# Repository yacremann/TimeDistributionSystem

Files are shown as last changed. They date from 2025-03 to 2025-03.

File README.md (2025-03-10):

# Time Distribution System for Lab Based Experiments

This project implements a time distribution system for laboratory based experiments using pulsed lasers.
It consists of a transmitter and several receivers. The transmitter generates a unique pulse-id number for
each laser pulse. This pulse-id, together with configuration information is transmitted to the receivers
over twisted-pair cables (use Cat 6A cables only!). A magnetic RAM is used to store the last value and to
recover after a power outage.

The receivers decode the pulse-id send it to FPGAs on individual instruments (framegrabber boards, digitizers, ...)
for time stamping the data. In addition, the receivers generate low-jitter trigger signals. These can be configured
from the transmitter.

The project contains the following components:
- Boards: Schematics and layouts of the printed circuit boards for the receiver and transmitter
- Firmware: Logic on the FPGAs as well as firmware running on an embedded RISC-V processor for the transmitter and receivers
- Tango: Device servers for the transmitter and to configure the trigger channels of the receivers (see tango-controls.org)
- Notes: Presentation with the block diagrams of the system

## Requirements:
- For simulating the individual components of the firmware: Cocotb, Verilator
- For synthesis: Quartus (intel) v. 23.1 standard edition
- For the software on the RISC-V: gcc for RV32IM (see https://github.com/SpinalHDL/VexRiscv)
- Tango control system: https://tango-controls.org

The project contains the following 3rd party components:
Firmware:
- CRC generator (https://github.com/hellgate202/crc_calc.git)
- Softcore: Based on the VexRiscV project (https://github.com/SpinalHDL/VexRiscv)
- TinyDuino_lib: developed by Domenic Wüthrich as a semester project at ETH Zurich, institute for integrated systems.
- fifo_v3: https://github.com/pulp-platform/common_cells/blob/master/src/fifo_v3.sv (ETH Zurich and University of Bologna)

License:
GNU Public License v3.0 (see LICENSE)

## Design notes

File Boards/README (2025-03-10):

This is the schematic and layout of the time distribution system. It consists of a transmitter and a receiver board. A detailed description will be published in a paper.

This part has been developed by Jingo Bozzini and Yves Acremann at the Physics Department of ETH Zurich, Switzerland.
acremann@solid.phys.ethz.ch

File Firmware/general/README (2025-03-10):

These components are often used by both, the receiver and transmitter (or by the receiver included in the framegrabber or digitizer).

8b10b: 8b 10b encoder / decoder
async_fifo: Async FIFO from https://github.com/dpretet/async_fifo (Copyright 2017 Damien Pretet ThotIP; See Github repo)
APB: Implementation of the APB bus and bus registers in SystemVerilog using interfaces.
CRC: CRC generator from https://github.com/hellgate202/crc_calc (Leonid Ivanov)
FrameReceiver: The receiver for decoding a data frame
FrequencyCounter: Used to measure the frequency of the laser oscillator
PayloadTransmitter: Prepares a data frame for serialization. It also calculates the CRC and performs 8b10b encoding.
protocol: The include file defining the data structure of a data frame
pulse_extender: Used to make the LEDs blink long enough in case of an error
SlowLink: Implements the slow transmitter (for sending data to the framegrabber) as well as CDR for the receiver in the framegrabber
Softcore: Microcontroller based on the VexRISCV CPU running on teh transmitter and receiver
Trigger: Circuit to generate the trigger sgnals at the output of the receiver
watchdog: Simple watchdog circuit to reset the receiver in case of a sequence of errors
FIFO: Fifo to cross clock domain boundaries (Copyright 2018 ETH Zurich and University of Bologna, https://github.com/pulp-platform/common_cells)

Most modules include a test bench using Cocotb and Verilator. These can be run using the Makefiles.

tinyduino_lib: Drivers for the components of the softcore (from Dominic Wüthrich, 2021)

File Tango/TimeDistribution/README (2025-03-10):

This is the Tango device server to control the time distribution
system through the USB port of the transmitter. It allows for 
configuring the receiver and setting the parameters of the
trigger outputs of the receivers.

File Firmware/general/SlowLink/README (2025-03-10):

This code implements the slow link between the receiver box and the receiver on the custom configurable FPGA on the frame grabber / digitizer.

It also contains test benches for simulating the CRD loop (50 MHz, 250 MHz and 312 MHz clock frequency) using Cocotb and Verilator.

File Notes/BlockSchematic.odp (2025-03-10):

## Block schematic

Low jitter time distribution system,

Y. Acremann, 2.2.2021

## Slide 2

Config data

80 MHz clk

Pulse-ID

100 Hz

M-RAM

MR25H128

FPGA

(MAX 10)

Logic,

CPU

LVDS to LVCMOS

SN65LVDS4

Transmitter

SPI

For precision receivers

80 MHz

AD9543

(jitter cleaner,

clk distribution)

SPI

Pulse-ID

8b/10b

Serializer

SCAN-

921025H

Fan-out

buffer

NB3L8504S

driver

DS15BA101

RJ-45

cable

driver

DS15BA101

RJ-45

cable

100 Hz

driver

DS15BA101

RJ-45

cable

UART,

JTAG

(CPU)

USB – Serial

FT2232

(for debugging)

driver

DS15BA101

RJ-45

cable

USB

800 Mbit/s signals with embedded clock

## Concept

- Bit clock synchronized to the oscillator (80 MHz) for precision timing (estimate: 10 ps jitter)
- Jitter cleaner to get very clean clock signals from 80 MHz clock
- FPGA:
- Counting of 100 Hz pulses (pulse-ID)
- Control of the serializer and M-RAM
- CPU for configuration of the jitter cleaner
- M-RAM: Stores the last pulse-ID (restore after power-loss)
- Distribution: RJ-45 cabes, max. length: 70m
- Encoding:
- For simple receivers: 10 Mbit/s 8b/10b encoded data => jitter: 100 ns
- For precision receivers: 800 Mbit/s 8b/10b encoded data (+ start bit)

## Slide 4

Config data (not time critical)

80 MHz clk

Pulse-id

100 Hz

Receiver

USB – Serial

FT2232

(for debugging)

FPGA

(MAX 10)

Logic,

CPU

USB

Input

RJ-45

cable

receiver (2x)

DS15EA101

De-Serializer

SCAN-

921226H

Pulse-id

Trigger

Time stamp

(to frame grabber)

Lock

AD9543

(jitter cleaner,

clk distribution)

SPI

RJ-45

cable

driver (2x)

DS15BA101

Low-jitter

trigger

Output to another receiver

LVDS to LVCMOS

SN65LVDS4

## Additional features: Receiver

- Power over the RJ-45 cable to the receivers
- Trigger outputs:
- Several independent outputs
- Low jitter
- Time steps in 1/(80 MHz)
- Output connector to connect another receiver

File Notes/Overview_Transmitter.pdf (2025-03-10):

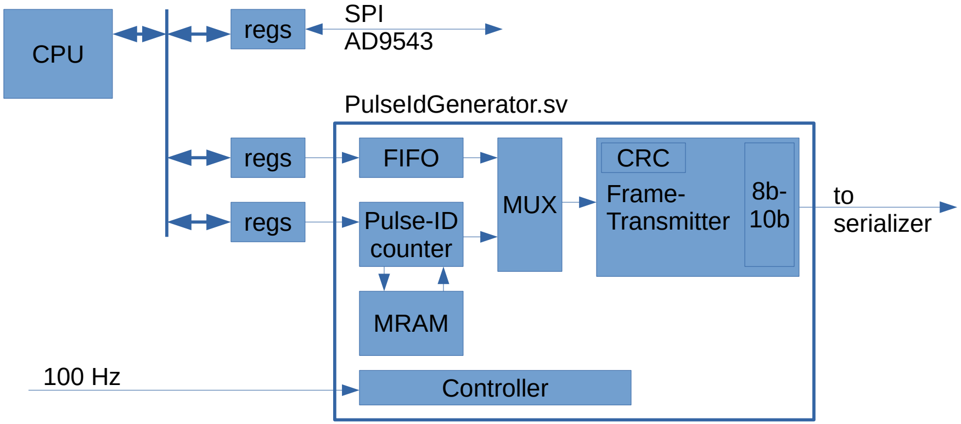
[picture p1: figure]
FIFO; Pulse-ID counter; MRAM; MUX; Controller; Frame- Transmitter; CRC; CPU; regs; to serializer; PulseIdGenerator.sv; SPI AD9543

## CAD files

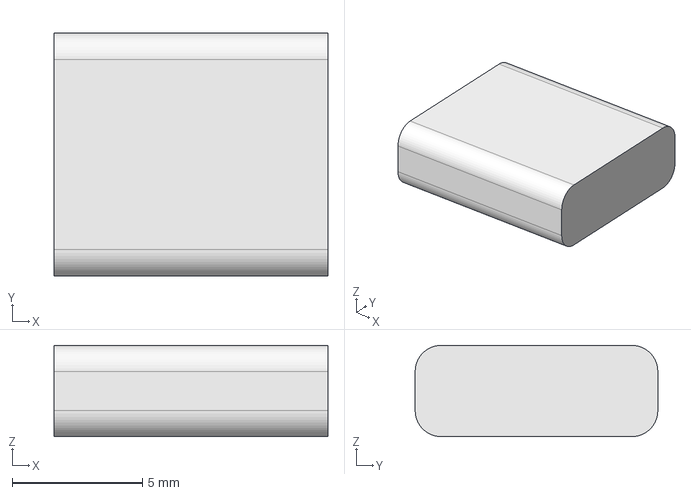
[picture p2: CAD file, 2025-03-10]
Boards/Receiver/3D_files/USB_C.step
10.5 x 9.30 x 3.50 mm

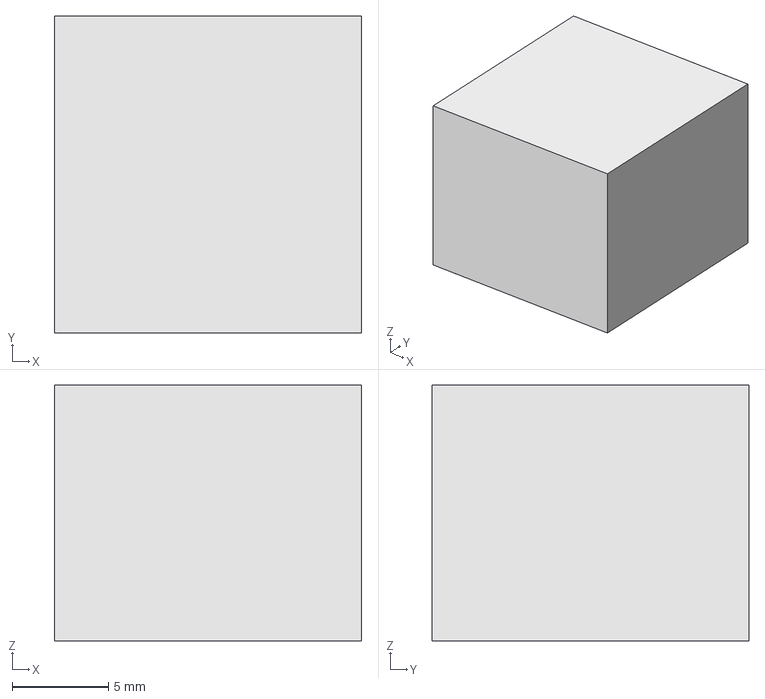
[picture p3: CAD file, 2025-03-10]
Boards/Transmitter/3D_files/RJ45.step
16.0 x 16.5 x 13.3 mm

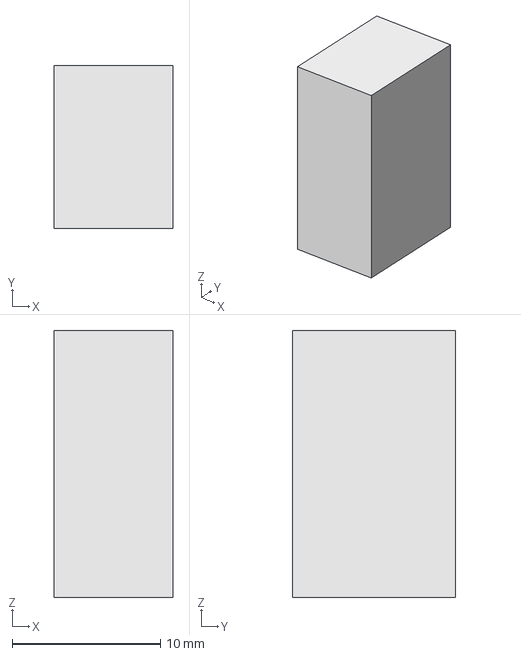
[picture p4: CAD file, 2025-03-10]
Boards/Transmitter/3D_files/conn_3.81mm.step
8.00 x 11.0 x 18.0 mm

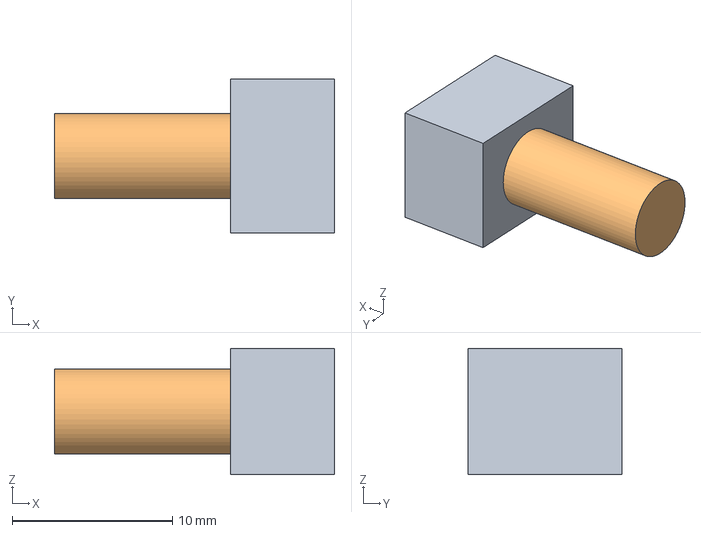
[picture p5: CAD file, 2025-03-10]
Boards/Receiver/3D_files/conn_sma.step
17.5 x 9.60 x 7.90 mm

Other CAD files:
Firmware/IdReceiver_DE10Lite/stp4.stp
Boards/Receiver/3D_files/RJ45.FCStd
Boards/Receiver/3D_files/USB_C.FCStd
Boards/Receiver/3D_files/conn_3.81mm.FCStd
Boards/Receiver/3D_files/conn_sma.FCStd
Boards/Transmitter/3D_files/RJ45.FCStd
Boards/Transmitter/3D_files/conn_3.81mm.FCStd

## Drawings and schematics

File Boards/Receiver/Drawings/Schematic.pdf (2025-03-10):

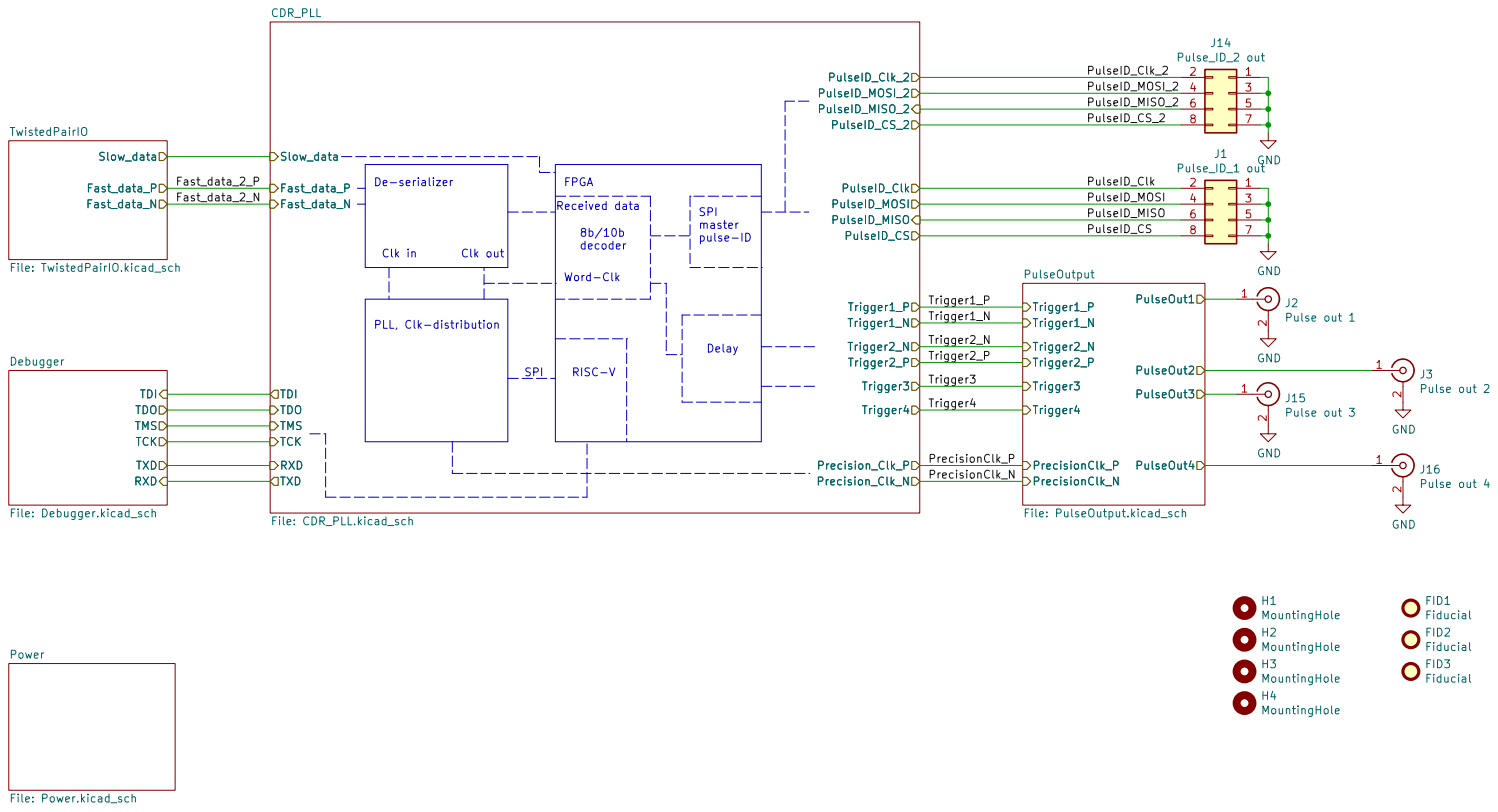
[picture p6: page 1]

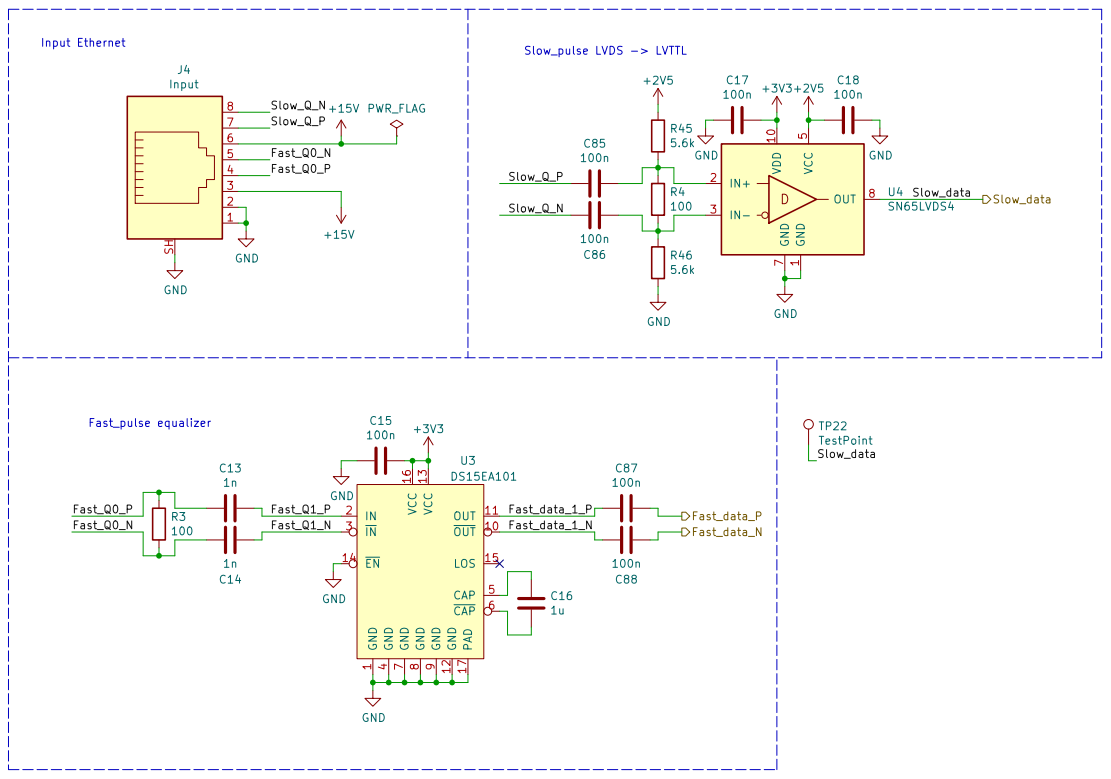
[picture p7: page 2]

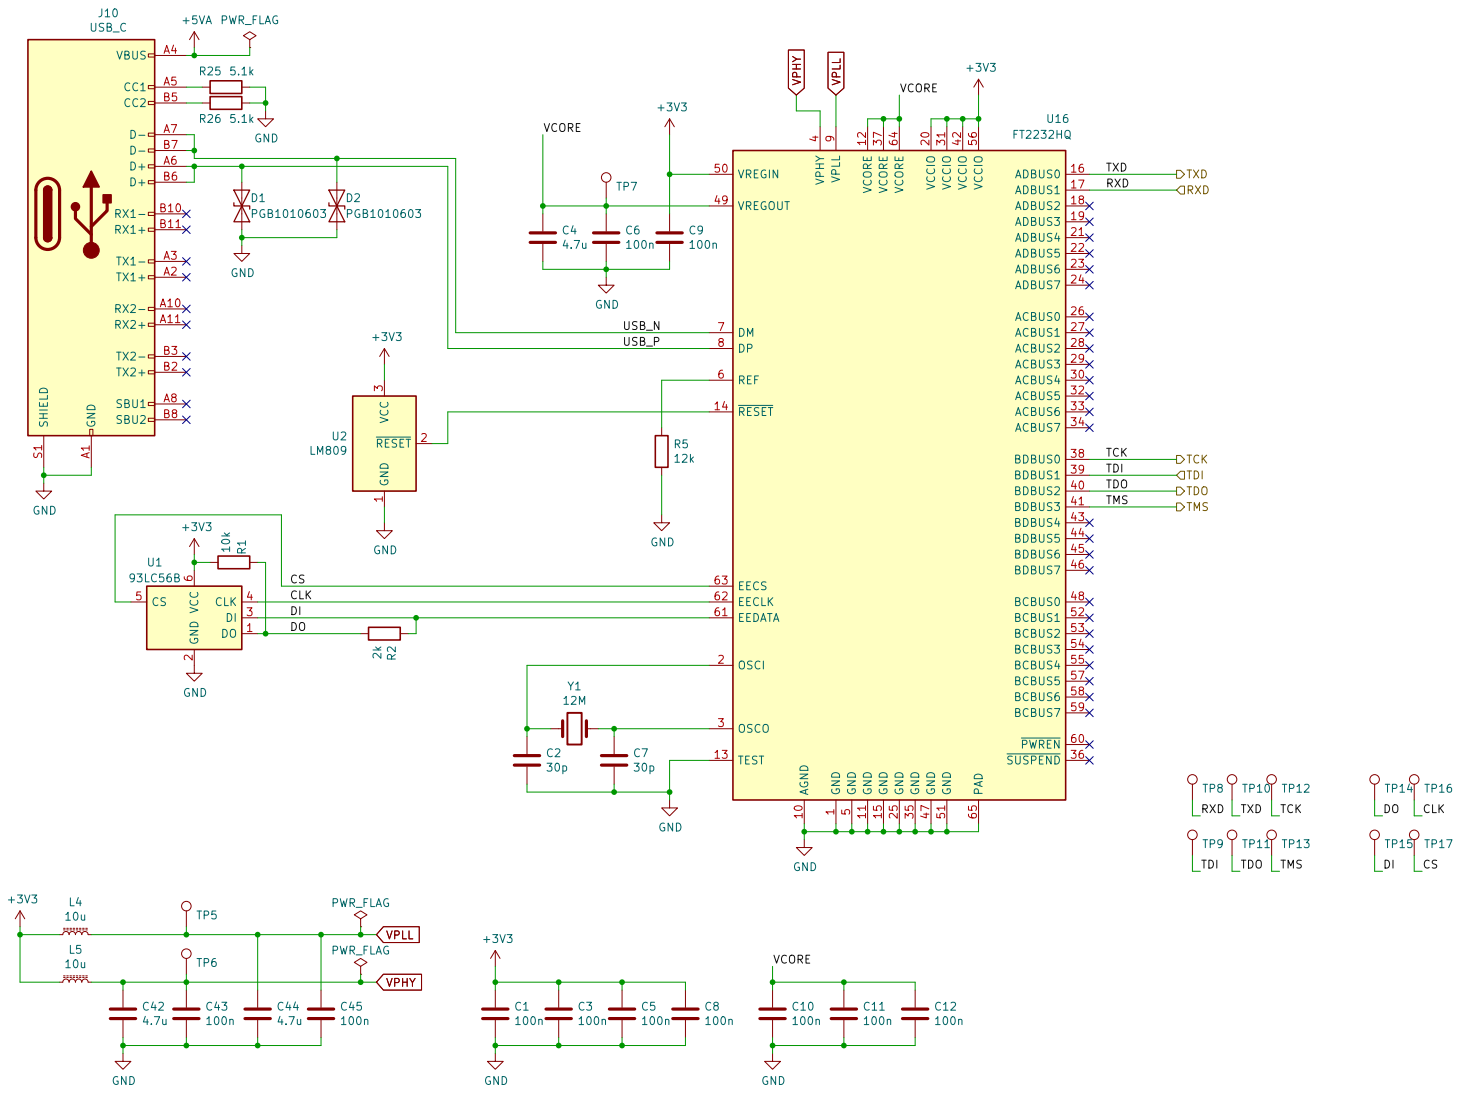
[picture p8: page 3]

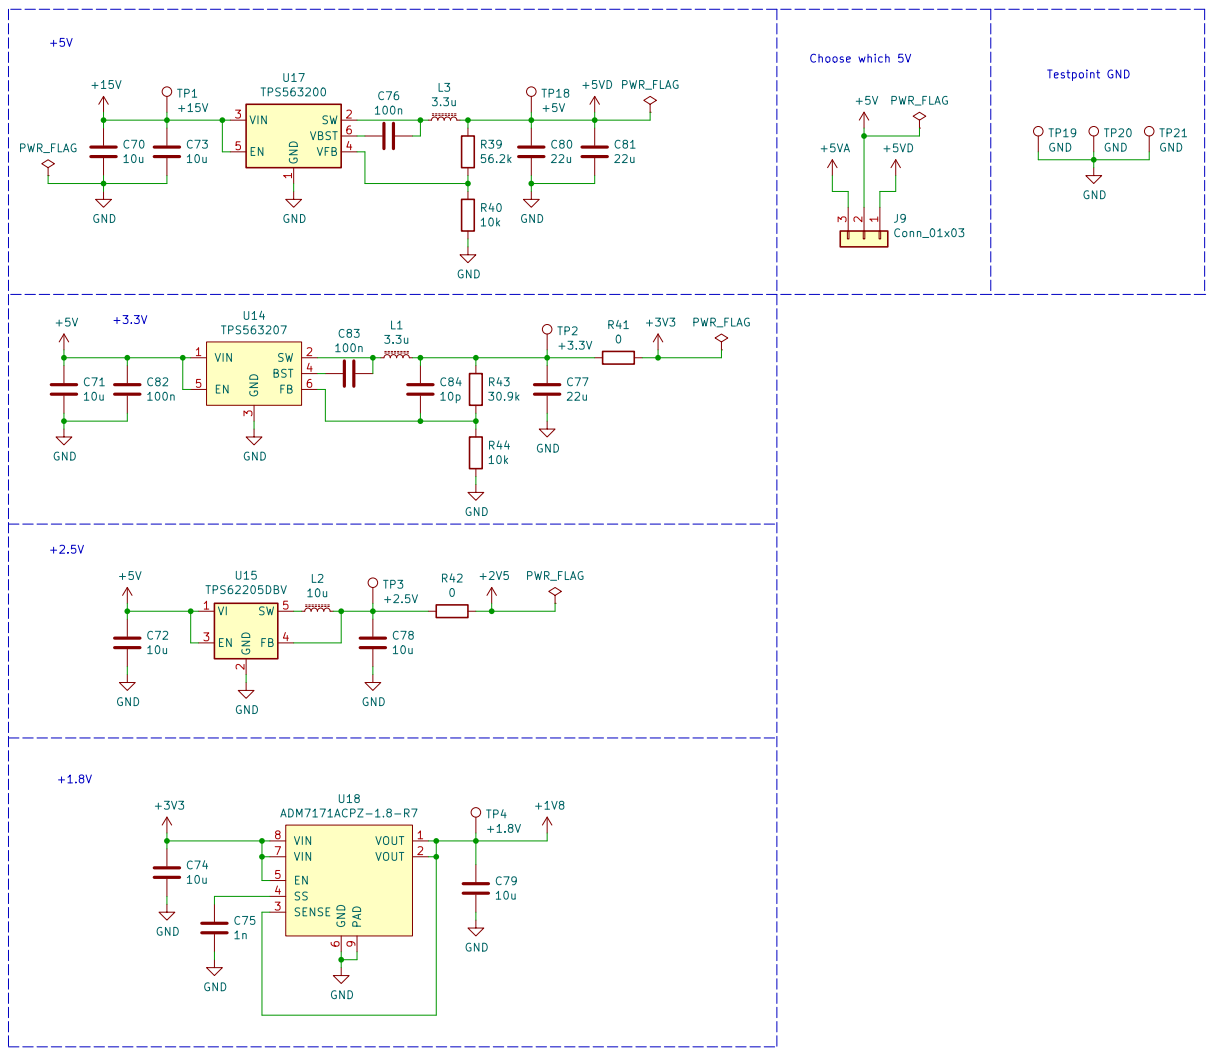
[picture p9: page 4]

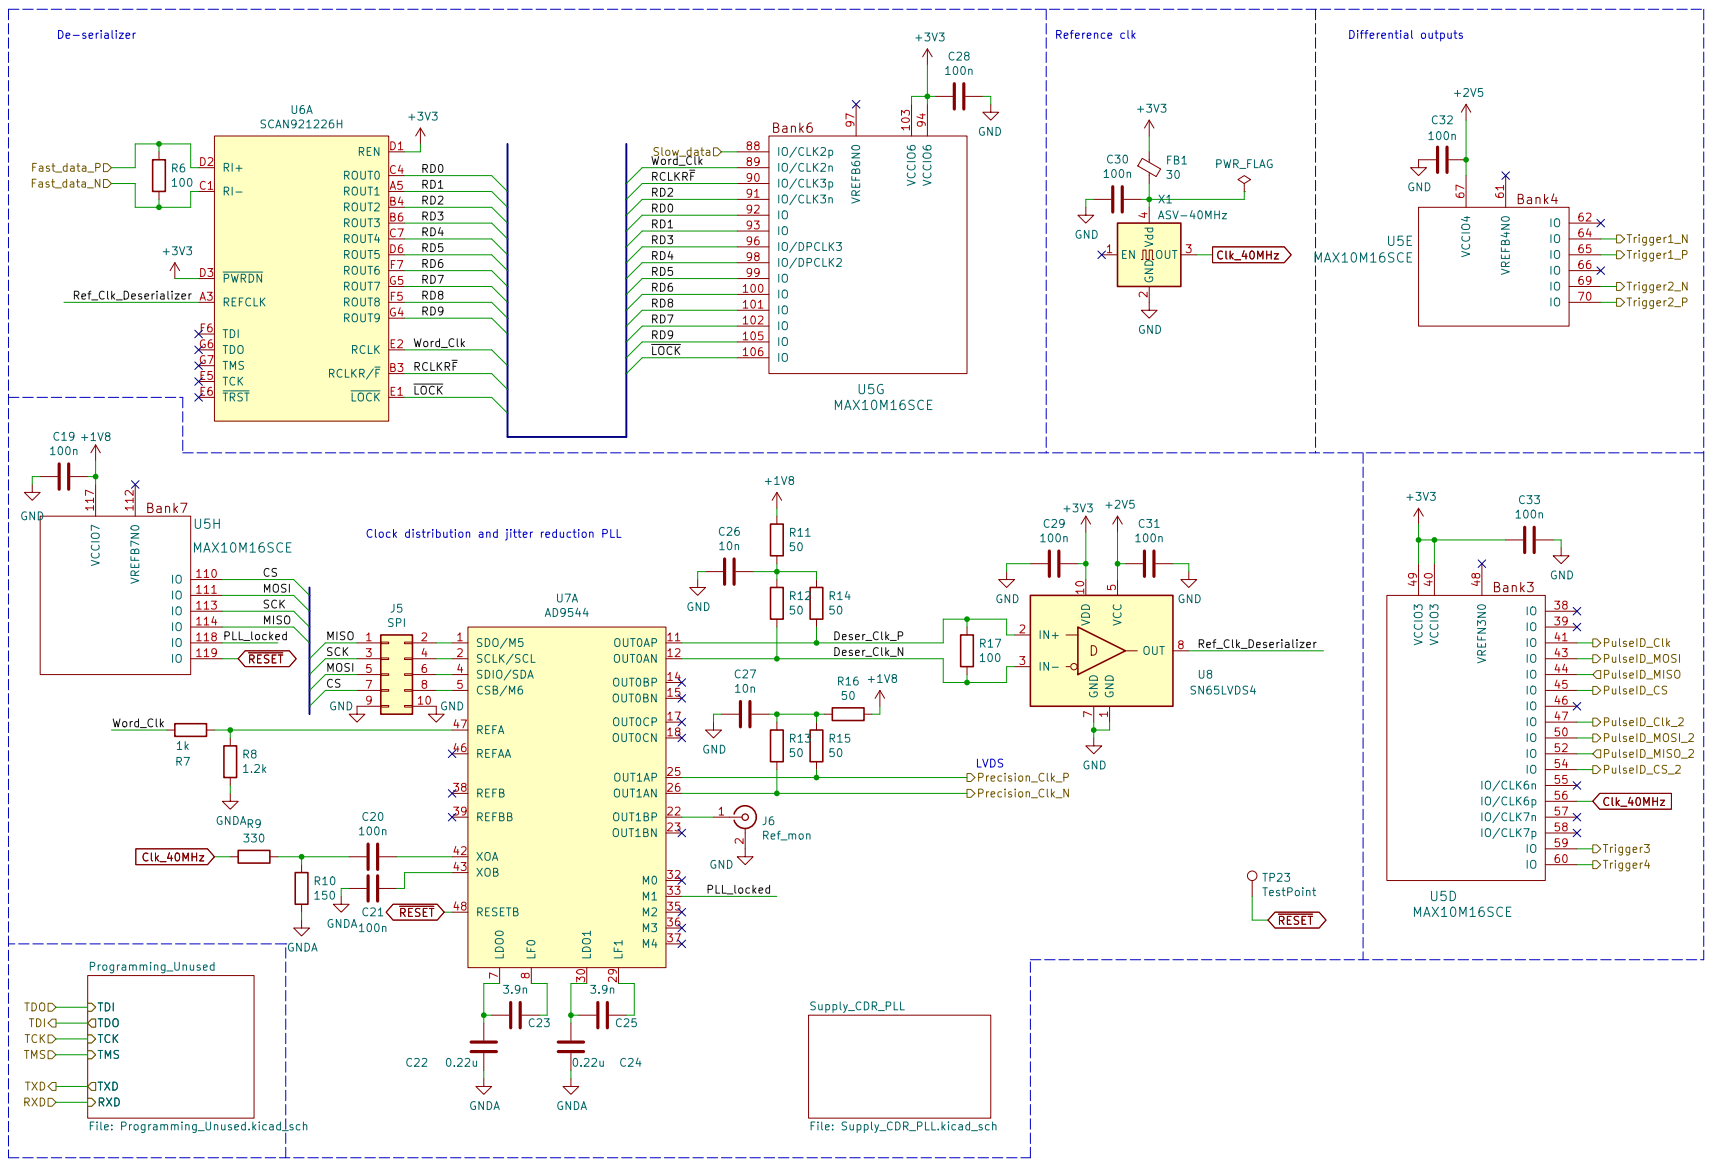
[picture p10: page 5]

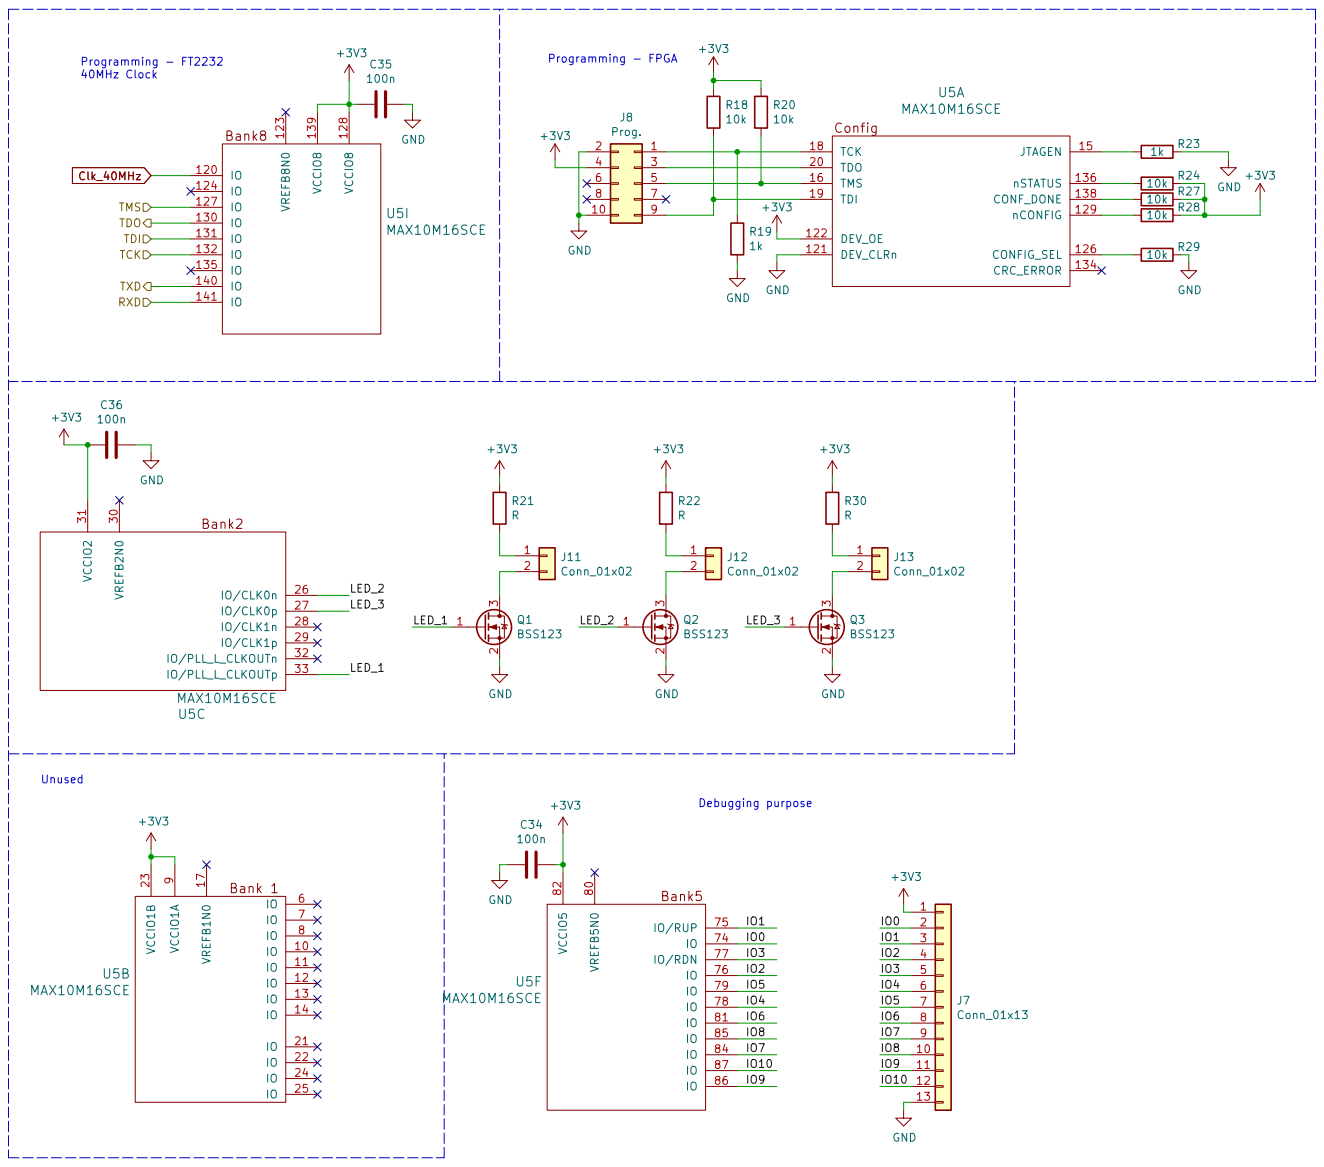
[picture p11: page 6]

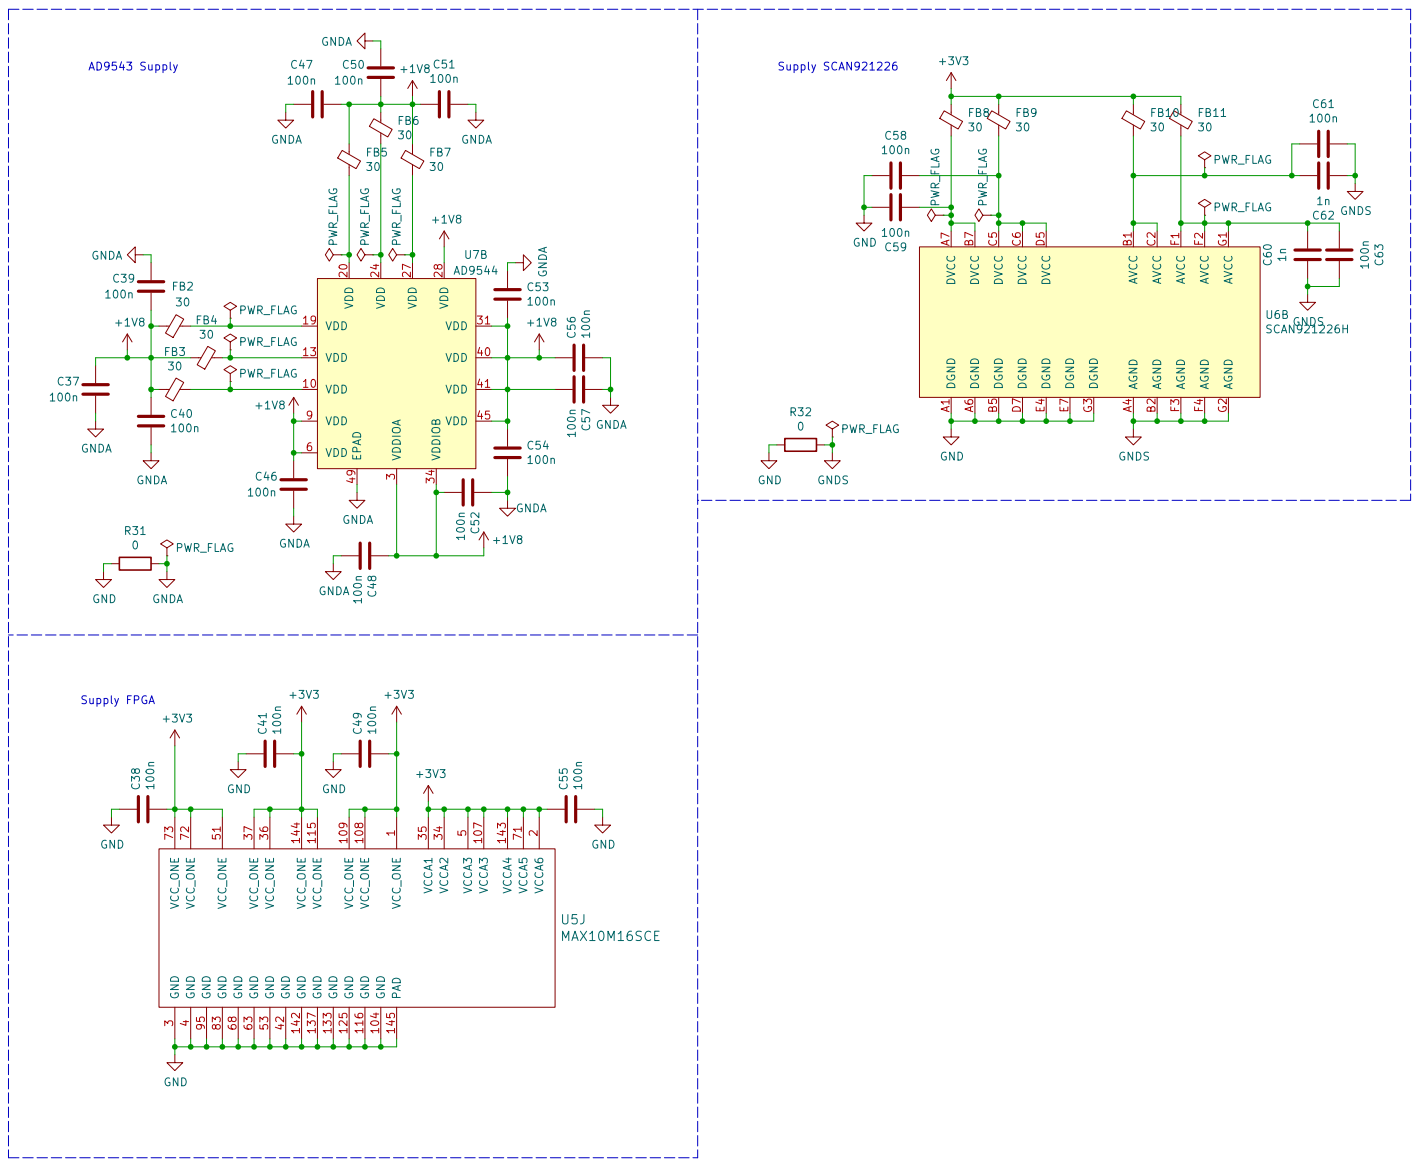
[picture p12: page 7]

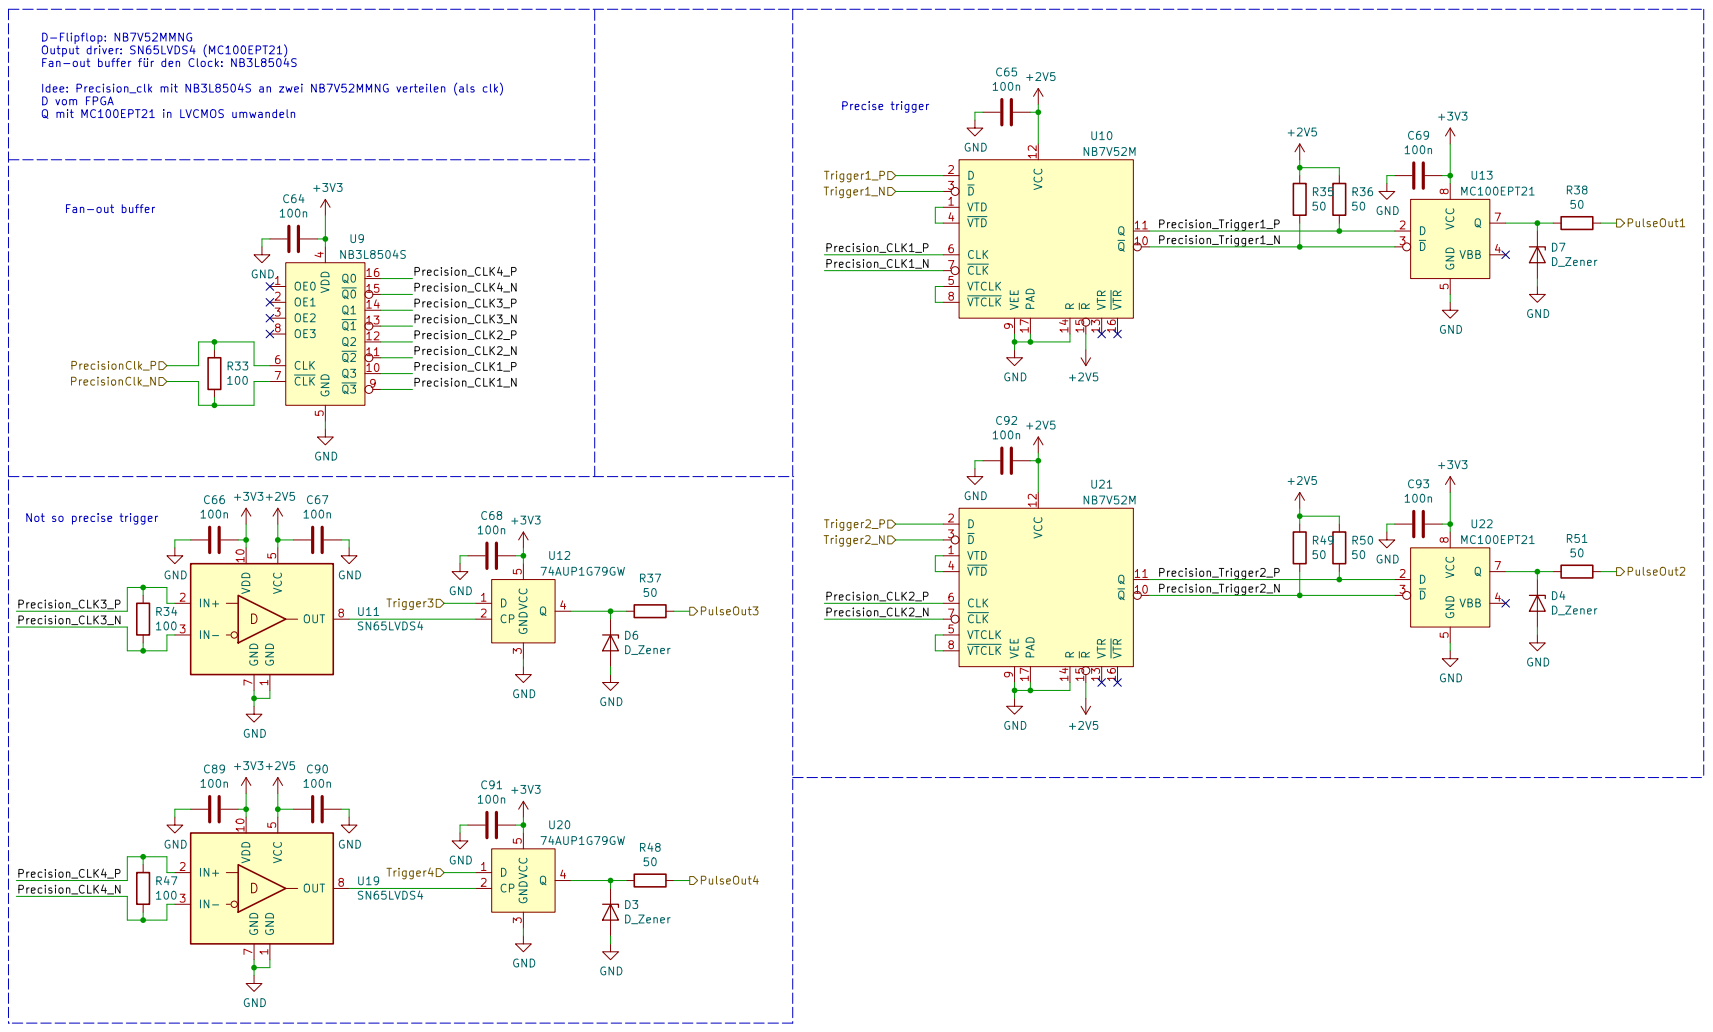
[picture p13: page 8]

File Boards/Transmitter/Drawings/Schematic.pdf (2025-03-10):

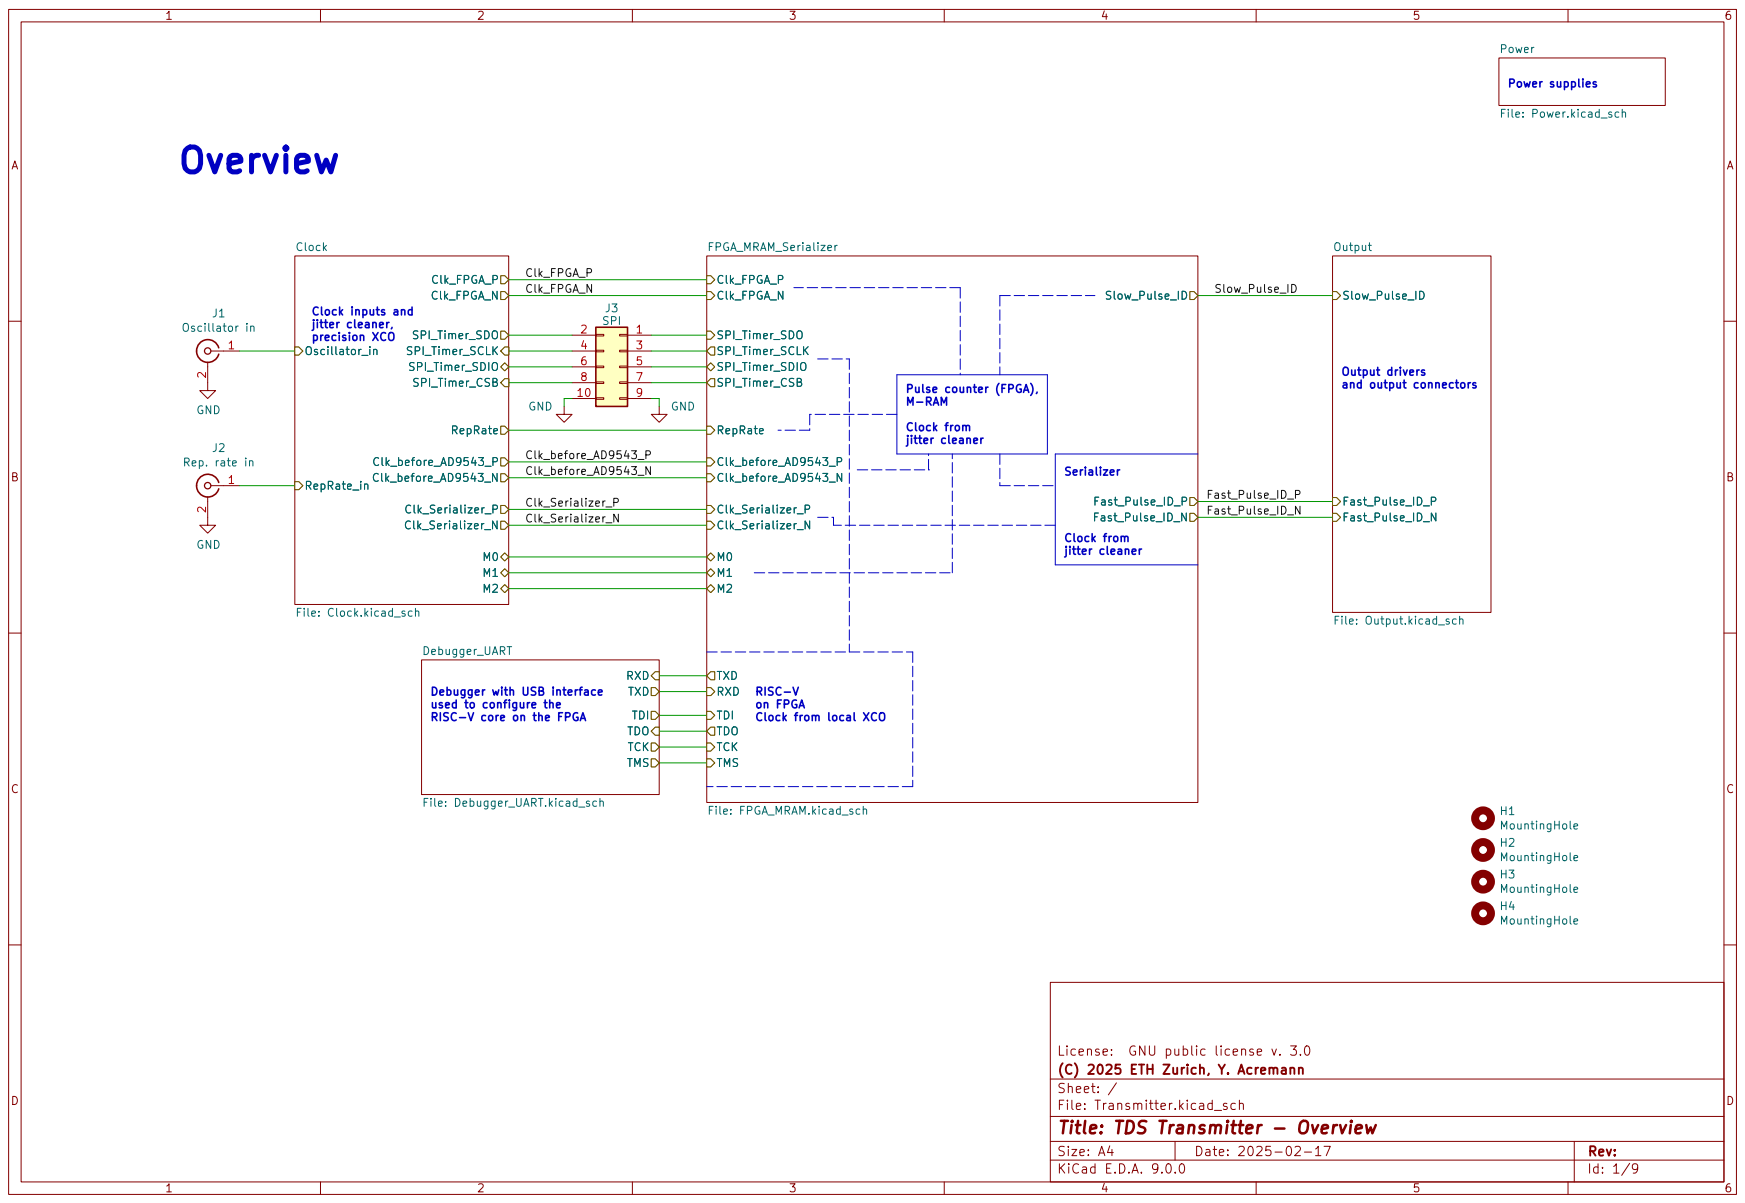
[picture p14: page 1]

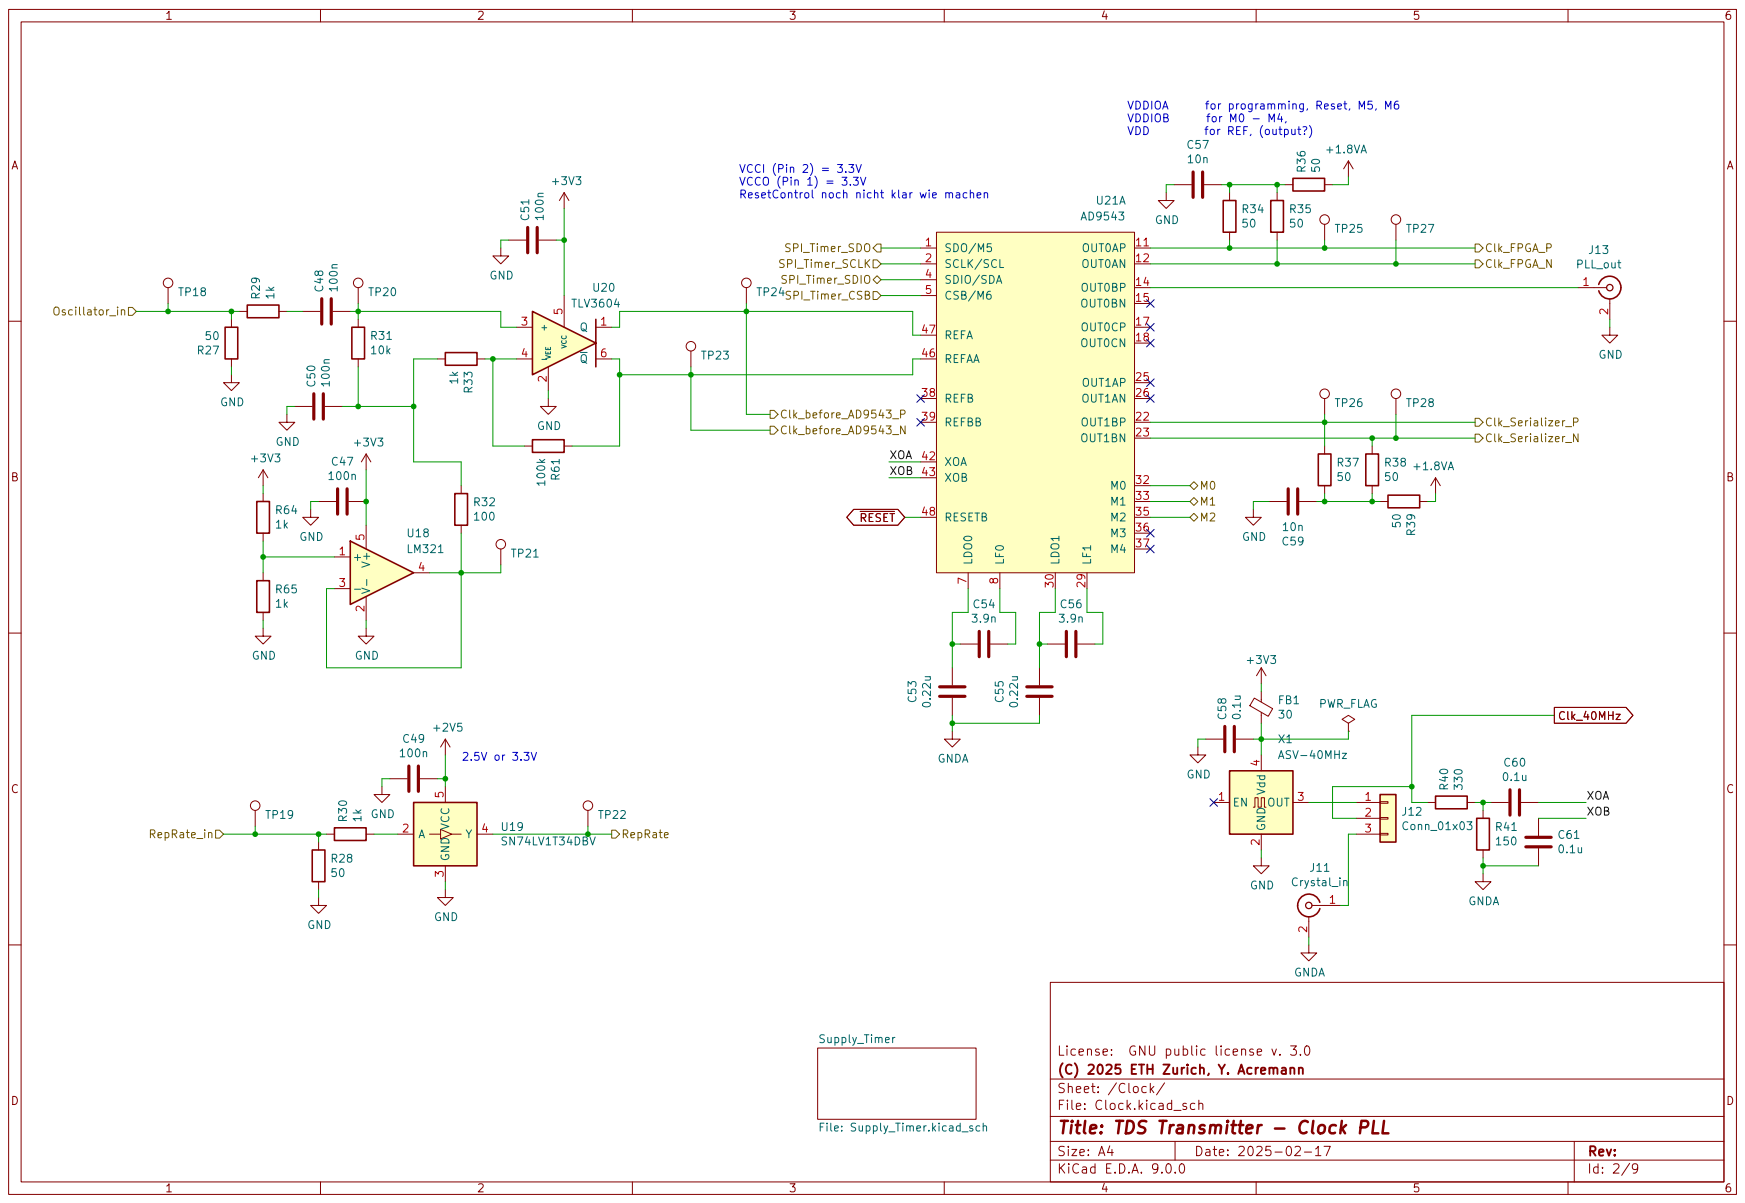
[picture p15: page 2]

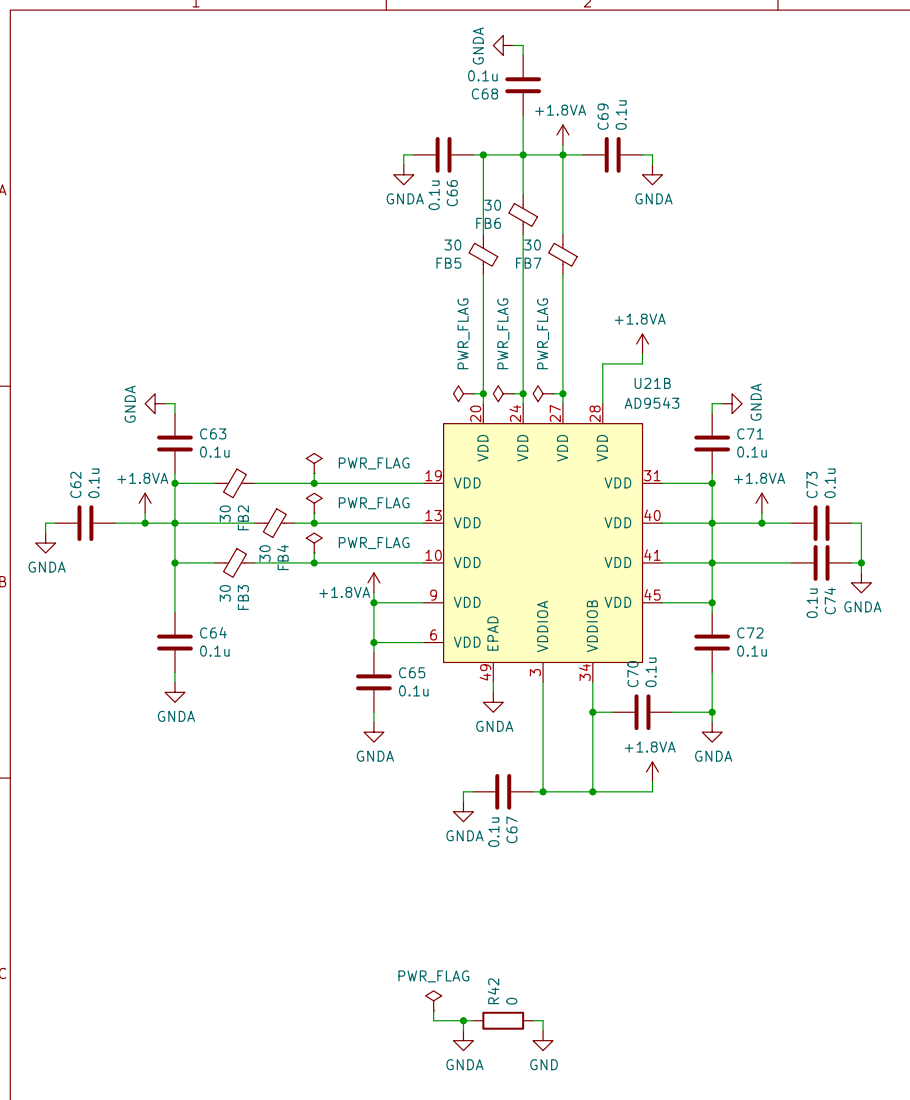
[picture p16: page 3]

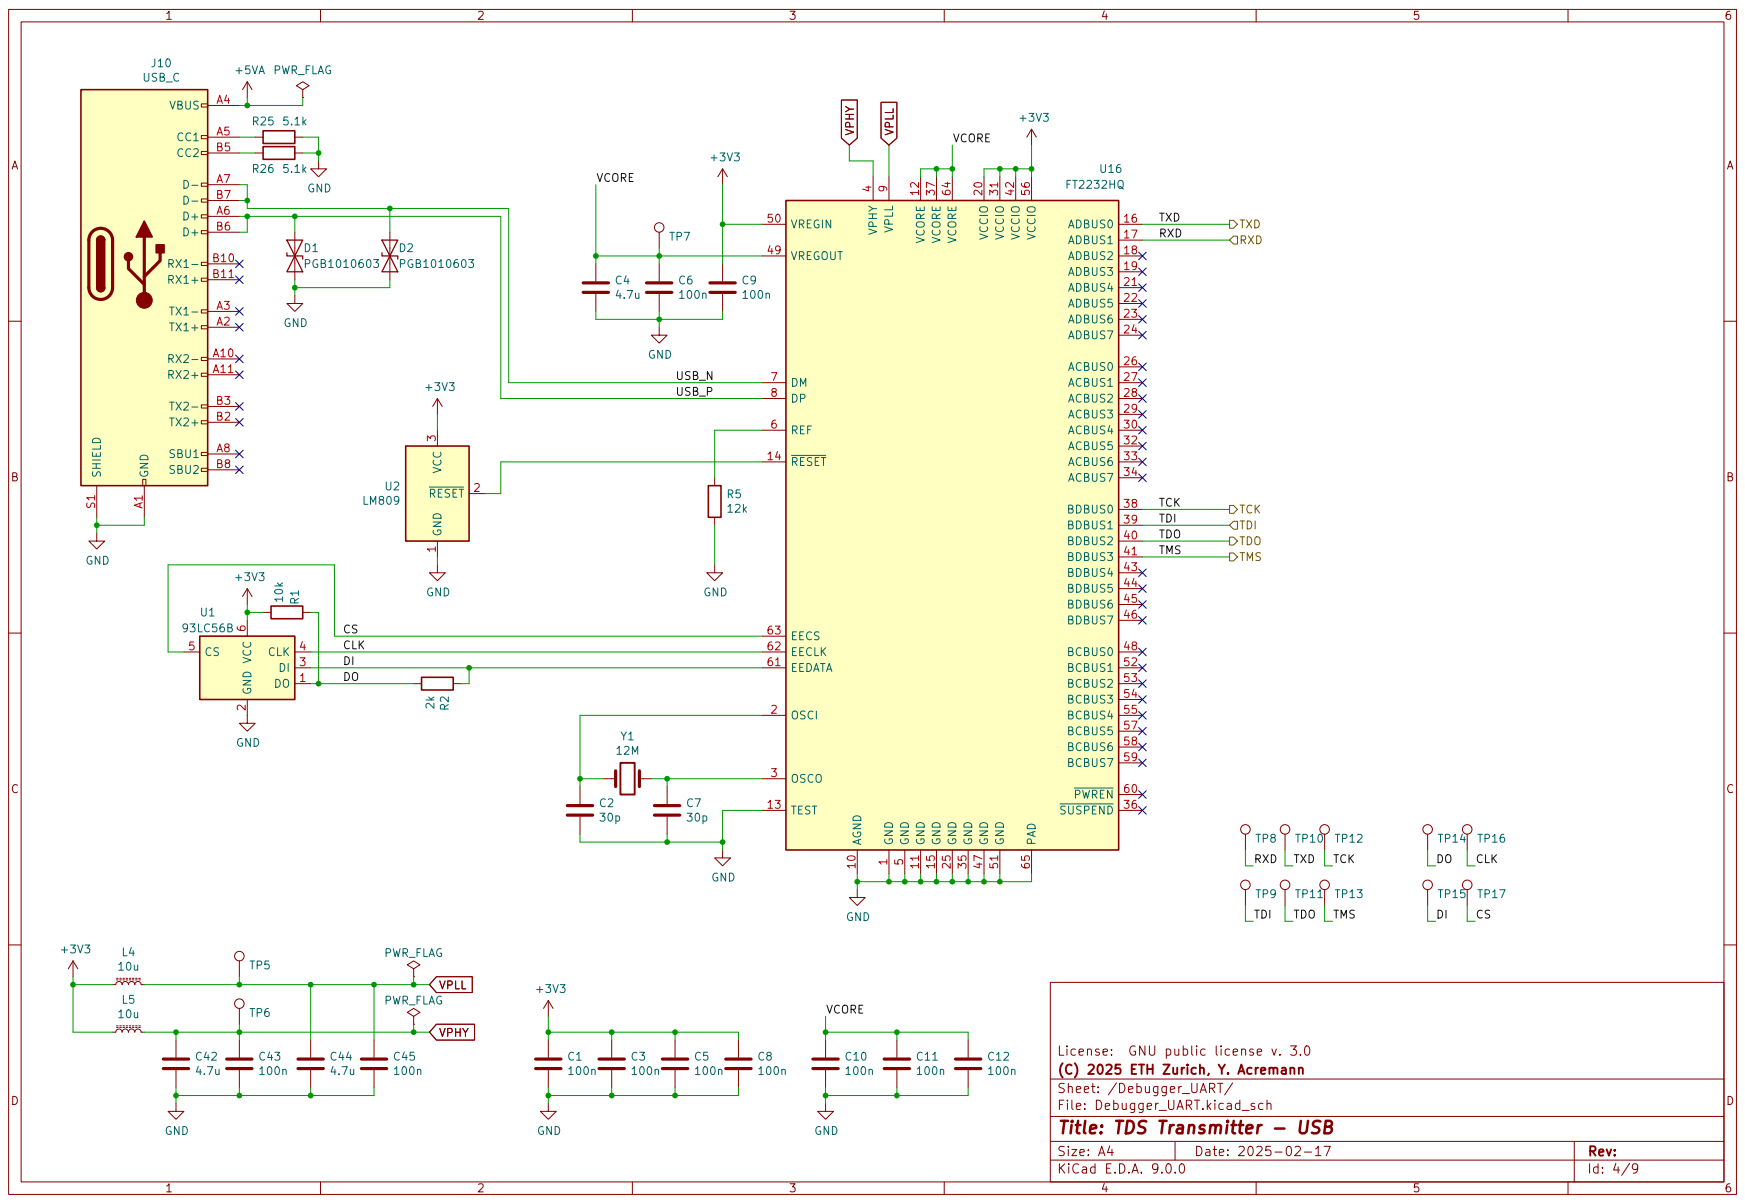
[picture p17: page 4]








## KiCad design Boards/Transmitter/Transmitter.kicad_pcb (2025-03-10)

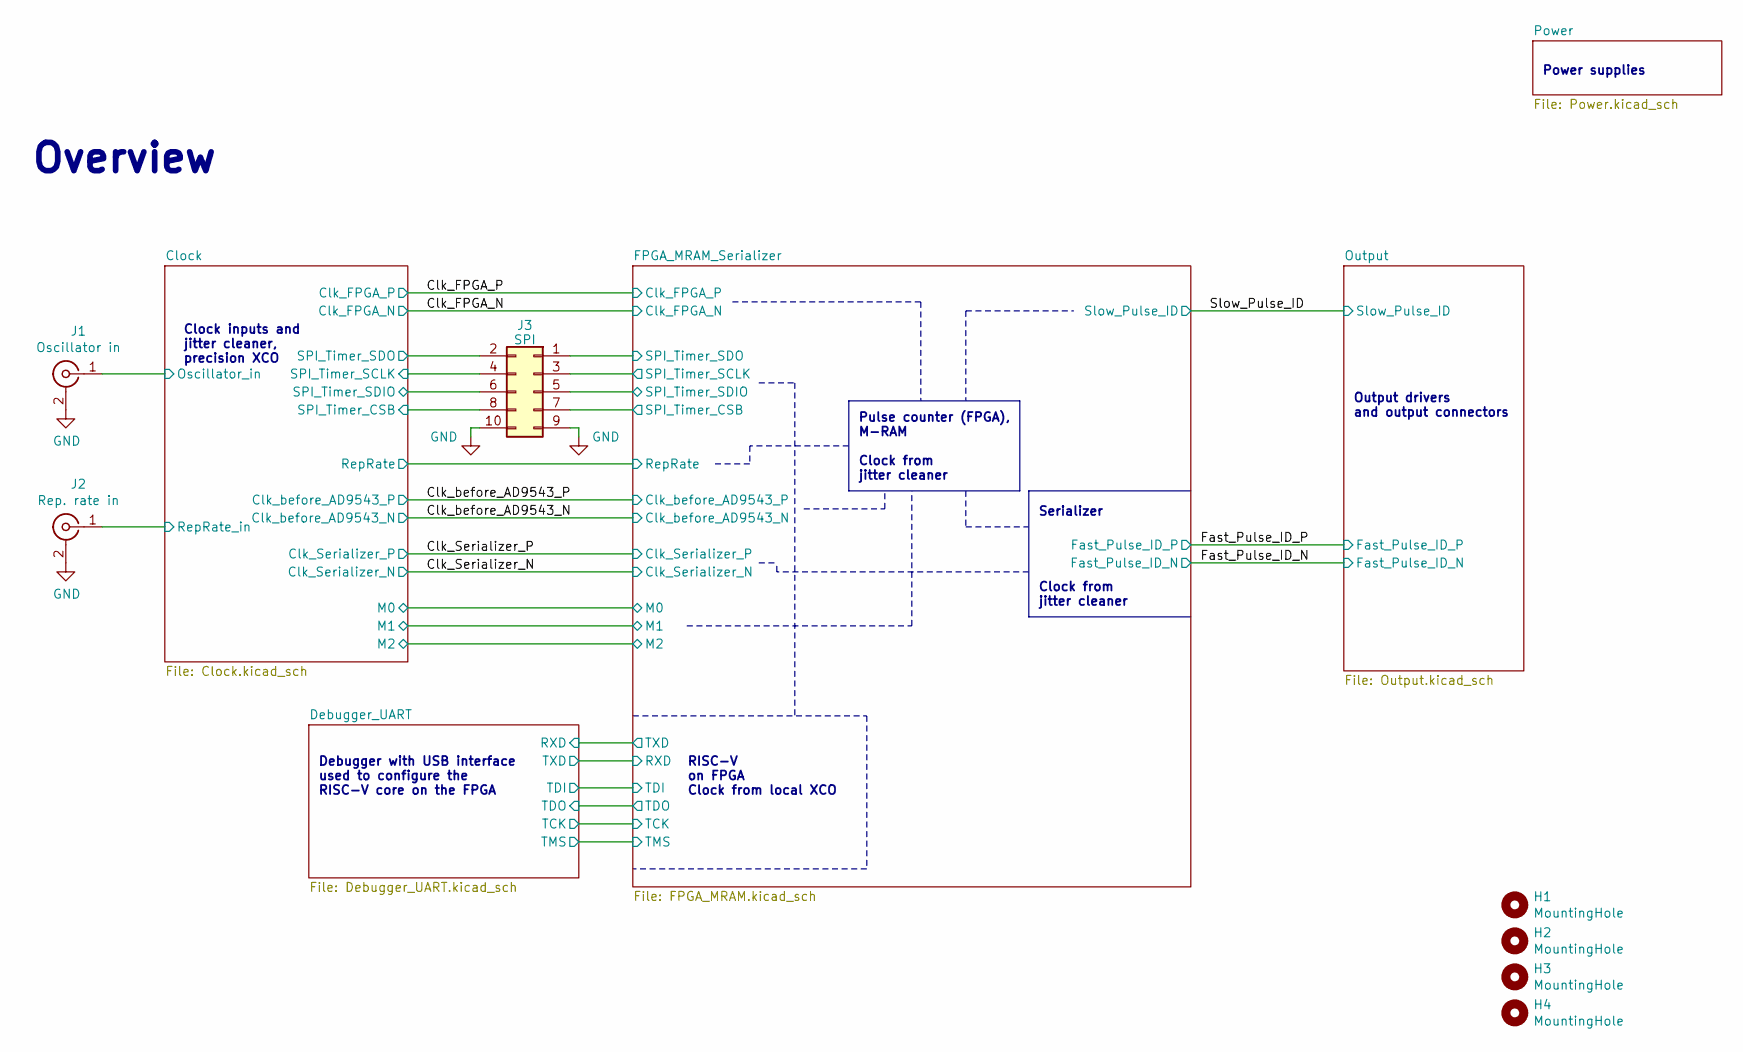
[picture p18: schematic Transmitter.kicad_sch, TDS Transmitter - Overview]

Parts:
H1, H2, H3, H4: MountingHole; MountingHole_2.7mm_M2.5
J1: Oscillator in; SMA_Amphenol_132289_EdgeMount
J2: Rep. rate in; SMA_Amphenol_132289_EdgeMount
J3: SPI; PinHeader_2x05_P2.54mm_Vertical

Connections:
/Clock/Oscillator_in: J1.1 (In); also elsewhere on the board
/Clock/RepRate_in: J2.1 (In); also elsewhere on the board
/Clock/SPI_Timer_CSB: J3.8; also elsewhere on the board
/Clock/SPI_Timer_SCLK: J3.4; also elsewhere on the board
/Clock/SPI_Timer_SDIO: J3.6; also elsewhere on the board
/Clock/SPI_Timer_SDO: J3.2; also elsewhere on the board
/FPGA_MRAM_Serializer/SPI_Timer_CSB: J3.7; also elsewhere on the board
/FPGA_MRAM_Serializer/SPI_Timer_SCLK: J3.3; also elsewhere on the board
/FPGA_MRAM_Serializer/SPI_Timer_SDIO: J3.5; also elsewhere on the board
/FPGA_MRAM_Serializer/SPI_Timer_SDO: J3.1; also elsewhere on the board
GND: J1.2 (Ext), J2.2 (Ext), J3.9, J3.10; also elsewhere on the board

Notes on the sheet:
RISC-V on FPGA Clock from local XCO
Pulse counter (FPGA), M-RAM Clock from jitter cleaner
Clock inputs and jitter cleaner, precision XCO
Clock from jitter cleaner
Overview
Power supplies
Debugger with USB interface used to configure the RISC-V core on the FPGA
Output drivers and output connectors
Serializer

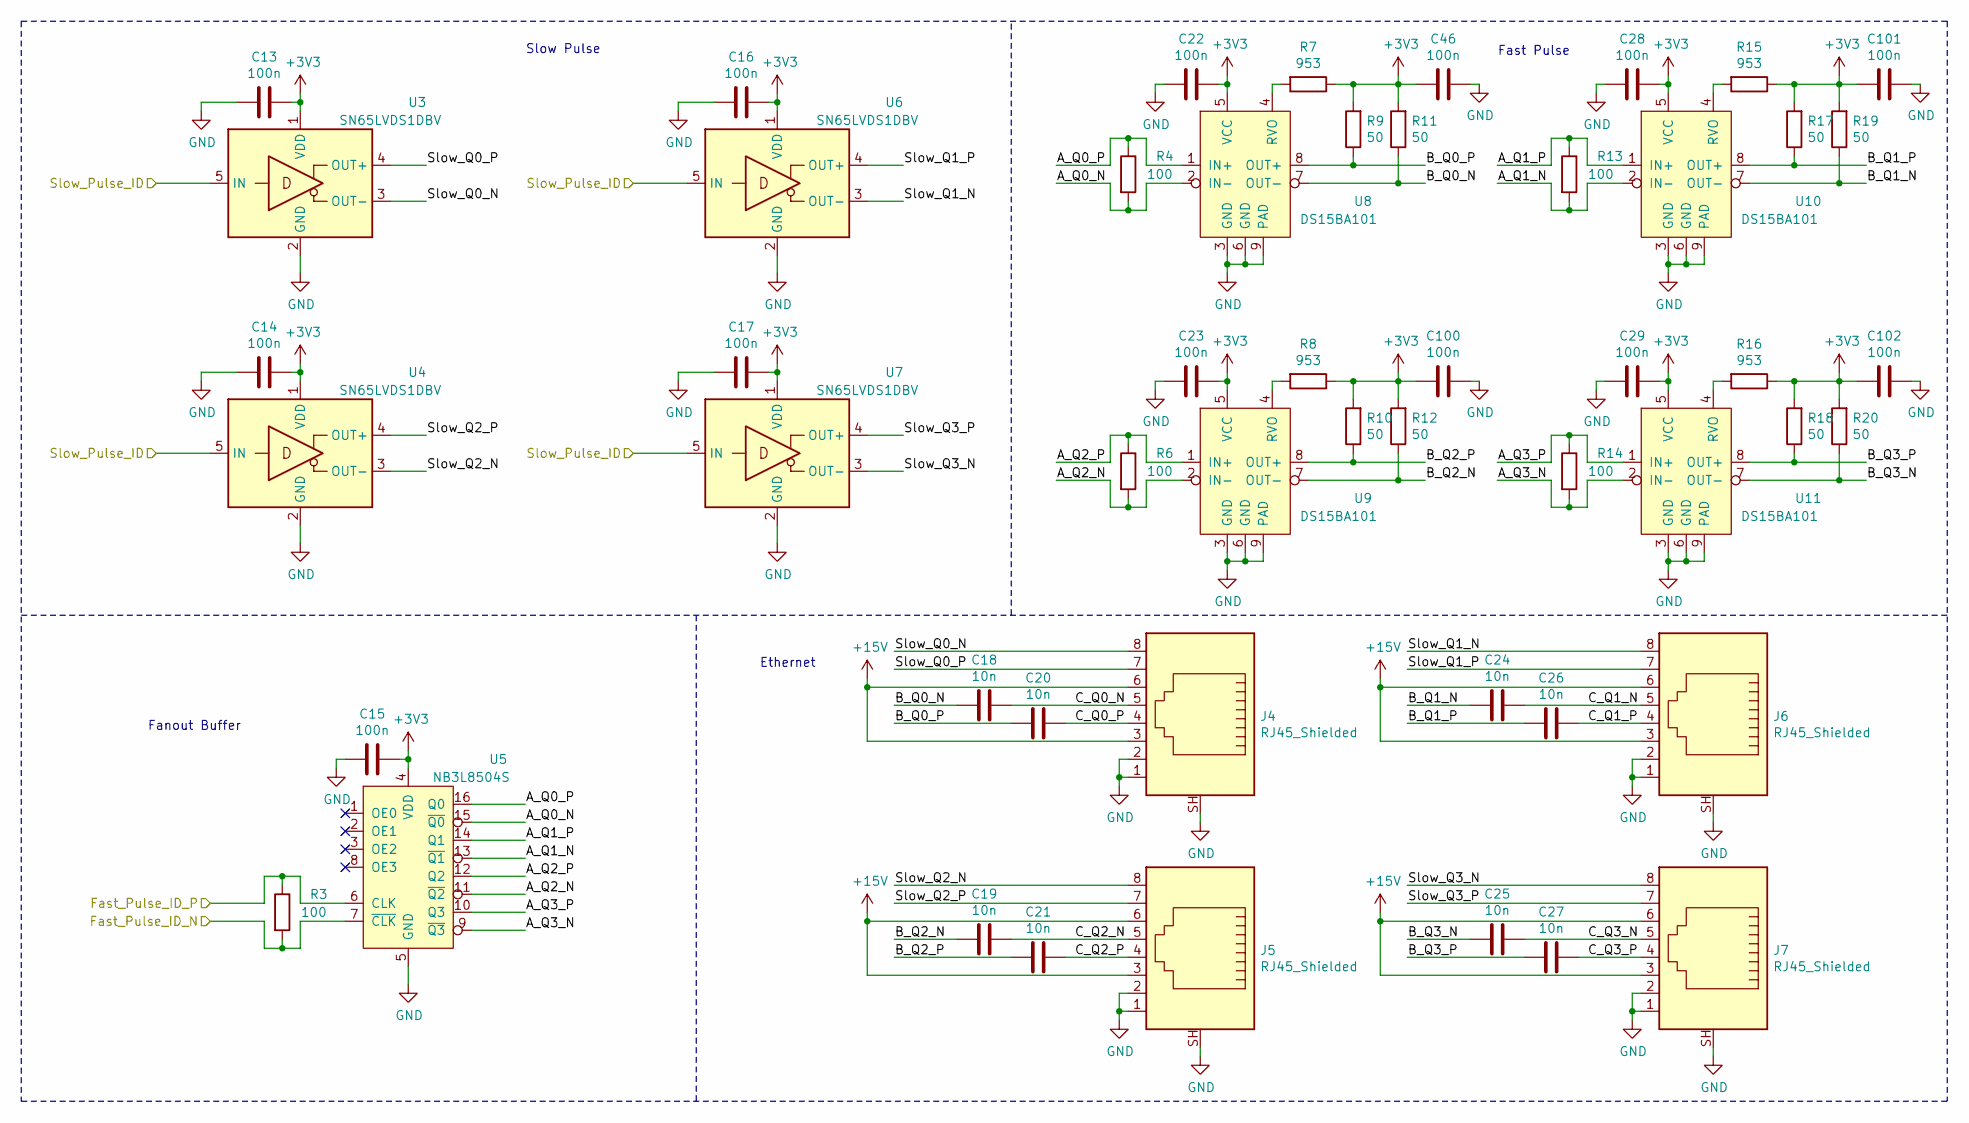
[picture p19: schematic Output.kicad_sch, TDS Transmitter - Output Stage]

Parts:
C13, C14, C15, C16, C17, C22, C23, C28, C29, C46, C100, C101, C102: 100n; C_0603_1608Metric
C18, C19, C20, C21, C24, C25, C26, C27: 10n; C_0603_1608Metric
J4, J5, J6, J7: RJ45_Shielded; RJ45_Amphenol_RJHSE5380
R3, R4, R6, R13, R14: 100; R_0402_1005Metric
R7, R8, R15, R16: 953; R_0603_1608Metric
R9, R10, R11, R12, R17, R18, R19, R20: 50; R_0603_1608Metric
U3, U4, U6, U7: SN65LVDS1DBV; SOT-23-5
U5: NB3L8504S; TSSOP-16_4.4x5mm_P0.65mm
U8, U9, U10, U11: DS15BA101; WSON-8-1EP_3x3mm_P0.5mm_EP1.6x2.0mm

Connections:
+3V3: C13.1, C14.1, C15.1, C16.1, C17.1, C22.1, C23.1, C28.1, C29.1, C46.2, C100.2, C101.2, C102.2, R7.1, R8.1, R9.2, R10.2, R11.2, R12.2, R15.1, R16.1, R17.2, R18.2, R19.2, R20.2, U3.1 (VDD), U4.1 (VDD), U5.4 (VDD), U6.1 (VDD), U7.1 (VDD), U8.5 (VCC), U9.5 (VCC), U10.5 (VCC), U11.5 (VCC); also elsewhere on the board
+15V: J4.3, J4.6, J5.3, J5.6, J6.3, J6.6, J7.3, J7.6; also elsewhere on the board
/Fast_Pulse_ID_N: R3.2, U5.7 (~CLK); also elsewhere on the board
/Fast_Pulse_ID_P: R3.1, U5.6 (CLK); also elsewhere on the board
/Output/A_Q0_N: R4.2, U5.15 (~Q0), U8.2 (IN-)
/Output/A_Q0_P: R4.1, U5.16 (Q0), U8.1 (IN+)
/Output/A_Q1_N: R13.2, U5.13 (~Q1), U10.2 (IN-)
/Output/A_Q1_P: R13.1, U5.14 (Q1), U10.1 (IN+)
/Output/A_Q2_N: R6.2, U5.11 (~Q2), U9.2 (IN-)
/Output/A_Q2_P: R6.1, U5.12 (Q2), U9.1 (IN+)
/Output/A_Q3_N: R14.2, U5.9 (~Q3), U11.2 (IN-)
/Output/A_Q3_P: R14.1, U5.10 (Q3), U11.1 (IN+)
/Output/B_Q0_N: C18.2, R11.1, U8.7 (OUT-)
/Output/B_Q0_P: C20.2, R9.1, U8.8 (OUT+)
/Output/B_Q1_N: C24.2, R19.1, U10.7 (OUT-)
/Output/B_Q1_P: C26.2, R17.1, U10.8 (OUT+)
/Output/B_Q2_N: C19.2, R12.1, U9.7 (OUT-)
/Output/B_Q2_P: C21.2, R10.1, U9.8 (OUT+)
/Output/B_Q3_N: C25.2, R20.1, U11.7 (OUT-)
/Output/B_Q3_P: C27.2, R18.1, U11.8 (OUT+)
/Output/C_Q0_N: C18.1, J4.5
/Output/C_Q0_P: C20.1, J4.4
/Output/C_Q1_N: C24.1, J6.5
/Output/C_Q1_P: C26.1, J6.4
/Output/C_Q2_N: C19.1, J5.5
/Output/C_Q2_P: C21.1, J5.4
/Output/C_Q3_N: C25.1, J7.5
/Output/C_Q3_P: C27.1, J7.4
/Output/Slow_Q0_N: J4.8, U3.3 (OUT-)
/Output/Slow_Q0_P: J4.7, U3.4 (OUT+)
/Output/Slow_Q1_N: J6.8, U6.3 (OUT-)
/Output/Slow_Q1_P: J6.7, U6.4 (OUT+)
/Output/Slow_Q2_N: J5.8, U4.3 (OUT-)
/Output/Slow_Q2_P: J5.7, U4.4 (OUT+)
/Output/Slow_Q3_N: J7.8, U7.3 (OUT-)
/Output/Slow_Q3_P: J7.7, U7.4 (OUT+)
/Slow_Pulse_ID: U3.5 (IN), U4.5 (IN), U6.5 (IN), U7.5 (IN); also elsewhere on the board
GND: C13.2, C14.2, C15.2, C16.2, C17.2, C22.2, C23.2, C28.2, C29.2, C46.1, C100.1, C101.1, C102.1, J4.1, J4.2, J4.SH, J5.1, J5.2, J5.SH, J6.1, J6.2, J6.SH, J7.1, J7.2, J7.SH, U3.2 (GND), U4.2 (GND), U5.5 (GND), U6.2 (GND), U7.2 (GND), U8.3 (GND), U8.6 (GND), U8.9 (PAD), U9.3 (GND), U9.6 (GND), U9.9 (PAD), U10.3 (GND), U10.6 (GND), U10.9 (PAD), U11.3 (GND), U11.6 (GND), U11.9 (PAD); also elsewhere on the board
unnamed: R7.2, U8.4 (RVO)
unnamed: R8.2, U9.4 (RVO)
unnamed: R15.2, U10.4 (RVO)
unnamed: R16.2, U11.4 (RVO)

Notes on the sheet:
Slow Pulse
Fanout Buffer
Fast Pulse
Ethernet

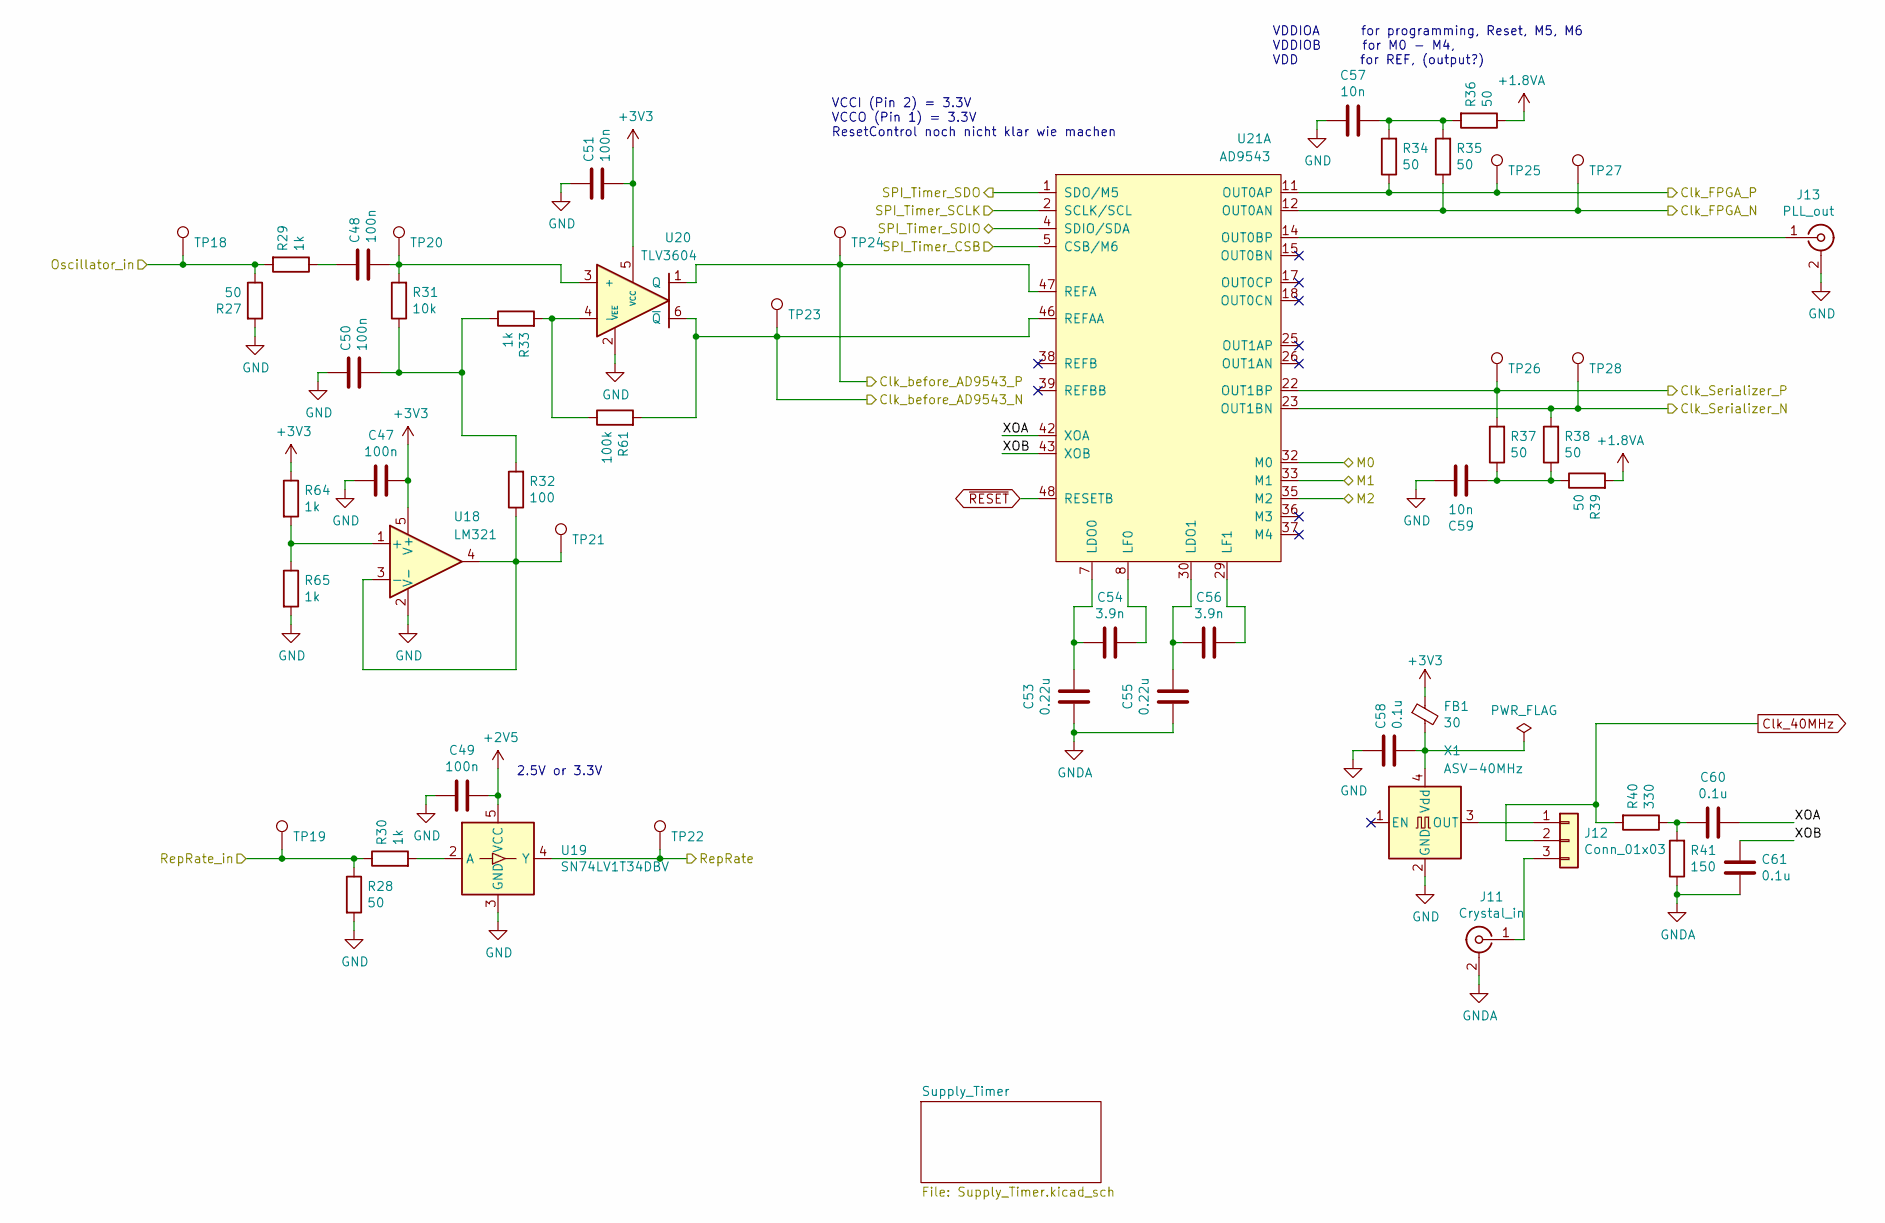
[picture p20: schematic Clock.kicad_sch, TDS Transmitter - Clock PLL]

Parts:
C47, C48, C49, C50, C51: 100n; C_0603_1608Metric
C53, C55: 0.22u; C_0603_1608Metric
C54, C56: 3.9n; C_0603_1608Metric
C57, C59: 10n; C_0603_1608Metric
C58: 0.1u; C_0603_1608Metric
C60, C61: 0.1u; C_0402_1005Metric
FB1: 30; L_0402_1005Metric
J11: Crystal_in; SMA_Amphenol_901-144_Vertical
J12: Conn_01x03; PinHeader_1x03_P2.54mm_Vertical
J13: PLL_out; SMA_Amphenol_901-144_Vertical
R27, R28, R34, R35, R36, R37, R38, R39: 50; R_0603_1608Metric
R29, R30, R33, R64, R65: 1k; R_0603_1608Metric
R31: 10k; R_0603_1608Metric
R32: 100; R_0603_1608Metric
R40: 330; R_0603_1608Metric
R41: 150; R_0603_1608Metric
R61: 100k; R_0603_1608Metric
TP18, TP19, TP20, TP21, TP22, TP23, TP24, TP25, TP26, TP27, TP28: TestPoint; TestPoint_THTPad_D1.5mm_Drill0.7mm
U18: LM321; SOT-353_SC-70-5_Handsoldering
U19: SN74LV1T34DBV; SOT-23-5
U20: TLV3604; R-PDSO-G6
U21: AD9543; LFCSP-48-1EP_7x7mm_P0.5mm_EP4.1x4.1mm
X1: ASV-40MHz; Oscillator_SMD_Abracon_ASV-4Pin_7.0x5.1mm

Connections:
+1V0: R36.1, R39.2; also elsewhere on the board
+2V5: C49.1, U19.5 (VCC); also elsewhere on the board
+3V3: C47.1, C51.2, FB1.1, R64.1, U18.5 (V+), U20.5 (VCC); also elsewhere on the board
/Clk_FPGA_N: R35.1, TP27.1, U21.12 (OUT0AN); also elsewhere on the board
/Clk_FPGA_P: R34.1, TP25.1, U21.11 (OUT0AP); also elsewhere on the board
/Clk_Serializer_N: R38.2, TP28.1, U21.23 (OUT1BN); also elsewhere on the board
/Clk_Serializer_P: R37.2, TP26.1, U21.22 (OUT1BP); also elsewhere on the board
/Clk_before_AD9543_N: R61.2, TP23.1, U20.6 (~Q), U21.46 (REFAA); also elsewhere on the board
/Clk_before_AD9543_P: TP24.1, U20.1 (Q), U21.47 (REFA); also elsewhere on the board
/Clock/M0: U21.32 (M0); also elsewhere on the board
/Clock/M1: U21.33 (M1); also elsewhere on the board
/Clock/M2: U21.35 (M2); also elsewhere on the board
/Clock/Oscillator_in: R27.1, R29.2, TP18.1; also elsewhere on the board
/Clock/RepRate: TP22.1, U19.4 (Y); also elsewhere on the board
/Clock/RepRate_in: R28.1, R30.1, TP19.1; also elsewhere on the board
/Clock/SPI_Timer_CSB: U21.5 (CSB/M6); also elsewhere on the board
/Clock/SPI_Timer_SCLK: U21.2 (SCLK/SCL); also elsewhere on the board
/Clock/SPI_Timer_SDIO: U21.4 (SDIO/SDA); also elsewhere on the board
/Clock/SPI_Timer_SDO: U21.1 (SDO/M5); also elsewhere on the board
/Clock/XOA: C60.1, U21.42 (XOA)
/Clock/XOB: C61.2, U21.43 (XOB)
Clk_40MHz: J12.2, R40.2; also elsewhere on the board
GND: C47.2, C49.2, C50.1, C51.1, C57.2, C58.2, C59.1, J13.2 (Ext), R27.2, R28.2, R65.2, U18.2 (V-), U19.3 (GND), U20.2 (VEE), X1.2 (GND); also elsewhere on the board
GNDA: C53.2, C55.2, C61.1, J11.2 (Ext), R41.1; also elsewhere on the board
unnamed: C48.1, R29.1
unnamed: C48.2, R31.2, TP20.1, U20.3 (+)
unnamed: C50.2, R31.1, R32.2, R33.1
unnamed: C53.1, C54.2, U21.7 (LDO0)
unnamed: C54.1, U21.8 (LF0)
unnamed: C55.1, C56.2, U21.30 (LDO1)
unnamed: C56.1, U21.29 (LF1)
unnamed: C57.1, R34.2, R35.2, R36.2
unnamed: C58.1, FB1.2, X1.4 (Vdd)
unnamed: C59.2, R37.1, R38.1, R39.1
unnamed: C60.2, R40.1, R41.2
unnamed: J11.1 (In), J12.3
unnamed: J12.1, X1.3 (OUT)
unnamed: J13.1 (In), U21.14 (OUT0BP)
unnamed: R30.2, U19.2 (A)
unnamed: R32.1, TP21.1, U18.3 (-), U18.4
unnamed: R33.2, R61.1, U20.4 (-)
unnamed: R64.2, R65.1, U18.1 (+)
~RESET: U21.48 (RESETB); also elsewhere on the board

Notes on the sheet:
2.5V or 3.3V
VDDIOA for programming, Reset, M5, M6 VDDIOB for M0 - M4, VDD for REF, (output?)
VCCI (Pin 2) = 3.3V VCCO (Pin 1) = 3.3V ResetControl noch nicht klar wie machen

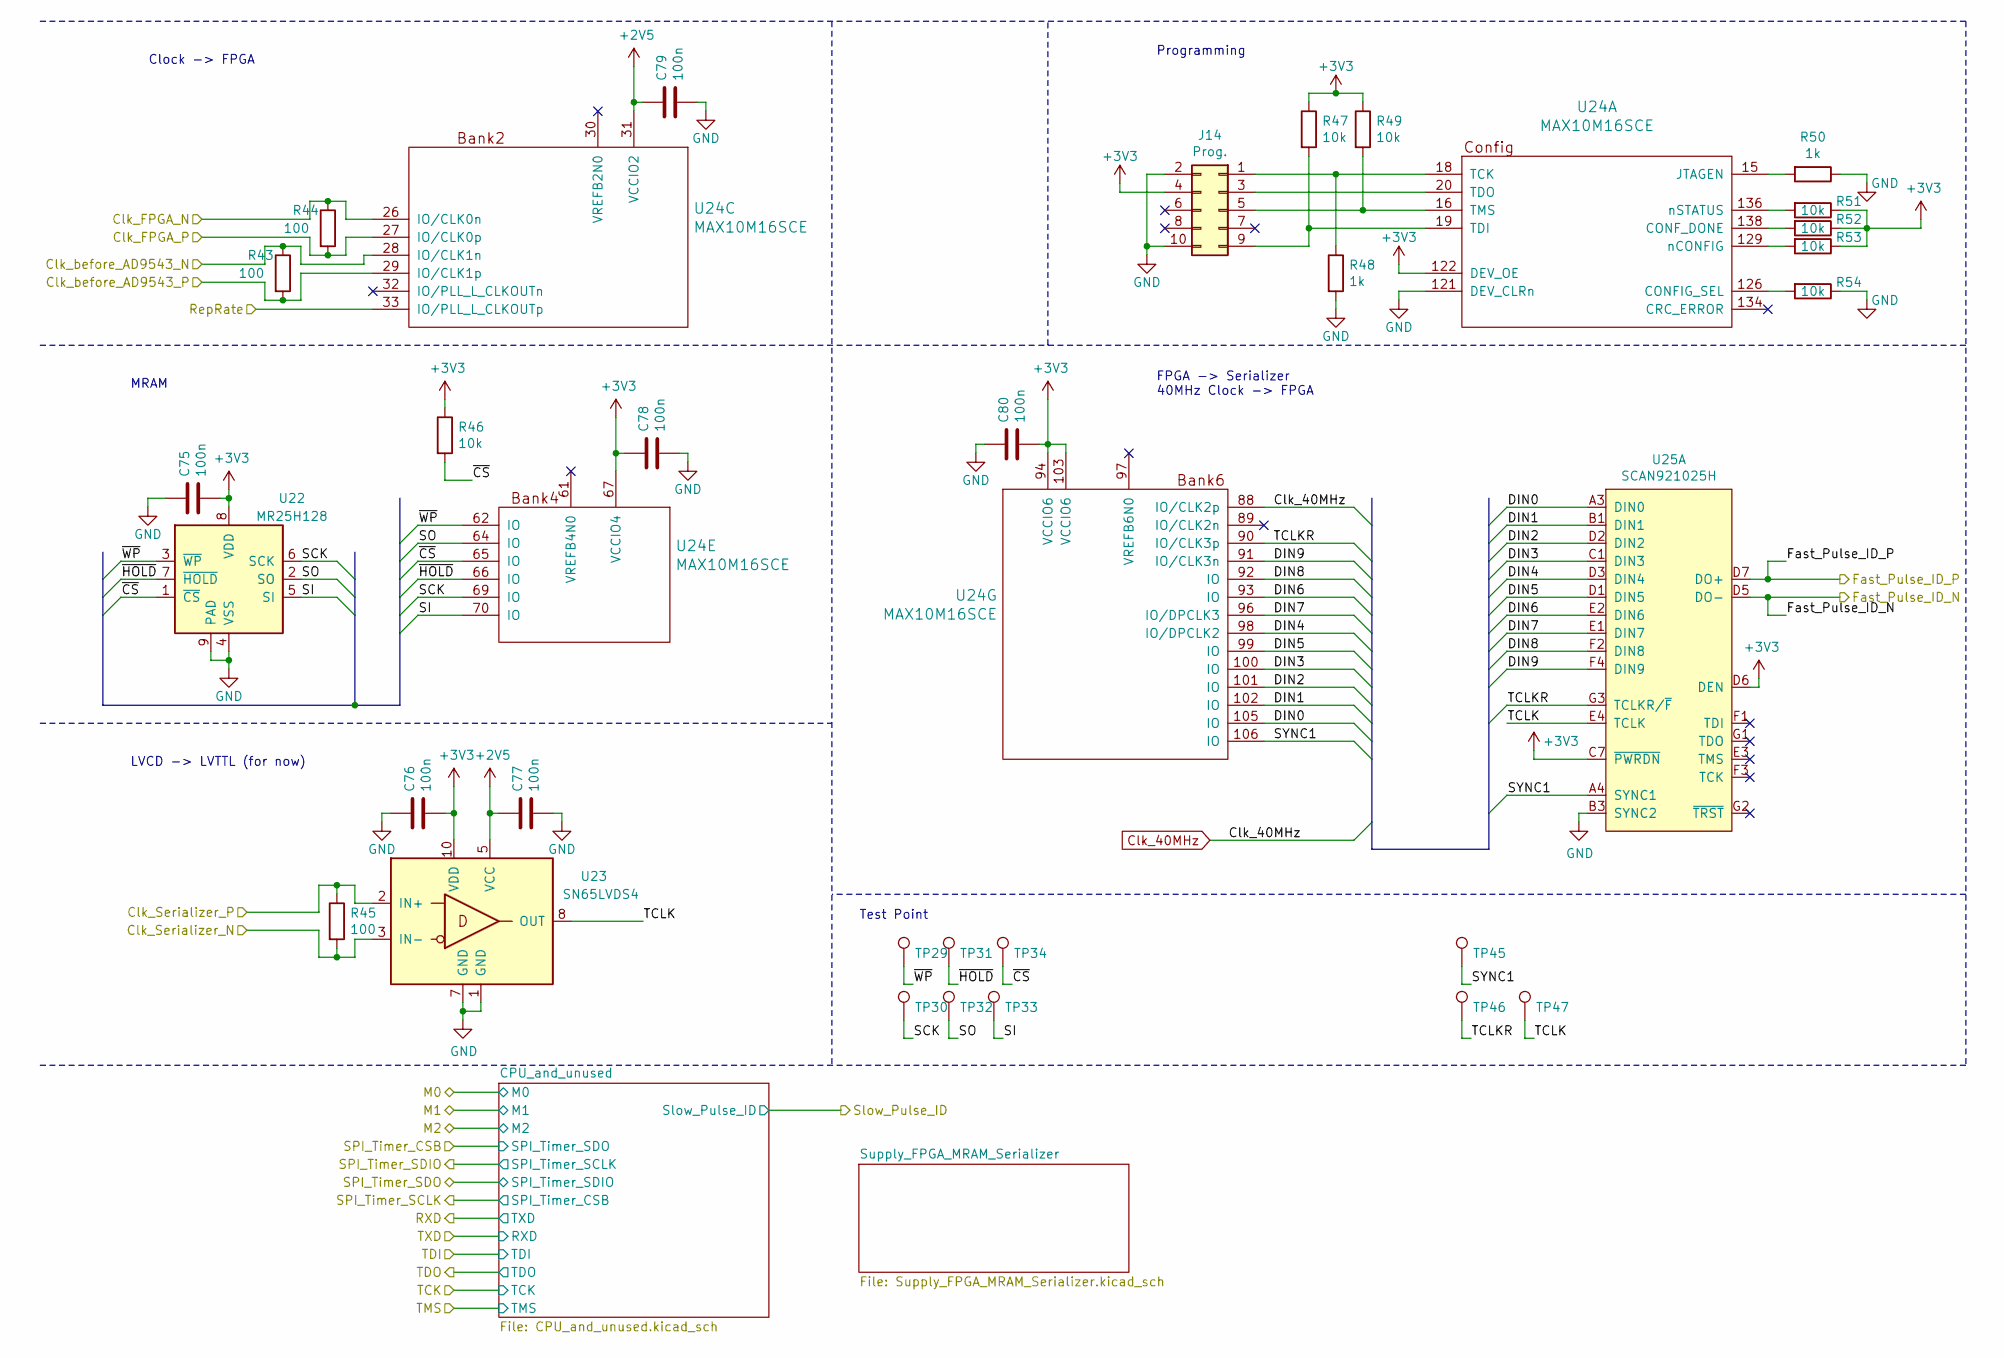
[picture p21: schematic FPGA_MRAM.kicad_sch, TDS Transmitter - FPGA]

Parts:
C75, C76, C77, C78, C79, C80: 100n; C_0603_1608Metric
J14: Prog.; IDC-Header_2x05_P2.54mm_Vertical
R43, R44, R45: 100; R_0402_1005Metric
R46, R47, R49, R51, R52, R53, R54: 10k; R_0603_1608Metric
R48, R50: 1k; R_0603_1608Metric
TP29, TP30, TP31, TP32, TP33, TP34, TP45, TP46, TP47: TestPoint; TestPoint_THTPad_D1.5mm_Drill0.7mm
U22: MR25H128; DFN-8-1EP_6x5mm_P1.27mm_EP2x2mm
U23: SN65LVDS4; Texas_R-PUQFN-N10
U24: MAX10M16SCE; EQFP_144
U25: SCAN921025H; BGA-49_7x7_7.0x7.0mm

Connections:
+2V5: C77.1, C79.1, U23.5 (VCC), U24.31 (VCCIO2); also elsewhere on the board
+3V3: C75.2, C76.2, C78.1, C80.2, J14.4, R46.1, R47.1, R49.1, R51.1, R52.1, R53.1, U22.8 (VDD), U23.10 (VDD), U24.67 (VCCIO4), U24.94 (VCCIO6), U24.103 (VCCIO6), U24.122 (DEV_OE), U25.C7 (~PWRDN), U25.D6 (DEN); also elsewhere on the board
/Clk_FPGA_N: R44.1, U24.26 (IO/CLK0n); also elsewhere on the board
/Clk_FPGA_P: R44.2, U24.27 (IO/CLK0p); also elsewhere on the board
/Clk_Serializer_N: R45.2, U23.3 (IN-); also elsewhere on the board
/Clk_Serializer_P: R45.1, U23.2 (IN+); also elsewhere on the board
/Clk_before_AD9543_N: R43.1, U24.28 (IO/CLK1n); also elsewhere on the board
/Clk_before_AD9543_P: R43.2, U24.29 (IO/CLK1p); also elsewhere on the board
/Clock/RepRate: U24.33 (IO/PLL_L_CLKOUTp); also elsewhere on the board
/FPGA_MRAM_Serializer/DIN0: U24.105 (IO), U25.A3 (DIN0)
/FPGA_MRAM_Serializer/DIN1: U24.102 (IO), U25.B1 (DIN1)
/FPGA_MRAM_Serializer/DIN2: U24.101 (IO), U25.D2 (DIN2)
/FPGA_MRAM_Serializer/DIN3: U24.100 (IO), U25.C1 (DIN3)
/FPGA_MRAM_Serializer/DIN4: U24.98 (IO/DPCLK2), U25.D3 (DIN4)
/FPGA_MRAM_Serializer/DIN5: U24.99 (IO), U25.D1 (DIN5)
/FPGA_MRAM_Serializer/DIN6: U24.93 (IO), U25.E2 (DIN6)
/FPGA_MRAM_Serializer/DIN7: U24.96 (IO/DPCLK3), U25.E1 (DIN7)
/FPGA_MRAM_Serializer/DIN8: U24.92 (IO), U25.F2 (DIN8)
/FPGA_MRAM_Serializer/DIN9: U24.91 (IO/CLK3n), U25.F4 (DIN9)
/FPGA_MRAM_Serializer/SCK: TP30.1, U22.6 (SCK), U24.69 (IO)
/FPGA_MRAM_Serializer/SI: TP33.1, U22.5 (SI), U24.70 (IO)
/FPGA_MRAM_Serializer/SO: TP32.1, U22.2 (SO), U24.64 (IO)
/FPGA_MRAM_Serializer/SYNC1: TP45.1, U24.106 (IO), U25.A4 (SYNC1)
/FPGA_MRAM_Serializer/TCLK: TP47.1, U23.8 (OUT), U25.E4 (TCLK)
/FPGA_MRAM_Serializer/TCLKR: TP46.1, U24.90 (IO/CLK3p), U25.G3 (TCLKR/~F)
/FPGA_MRAM_Serializer/~CS: R46.2, TP34.1, U22.1 (~CS), U24.65 (IO)
/FPGA_MRAM_Serializer/~HOLD: TP31.1, U22.7 (~HOLD), U24.66 (IO)
/FPGA_MRAM_Serializer/~WP: TP29.1, U22.3 (~WP), U24.62 (IO)
/Fast_Pulse_ID_N: U25.D5 (DO-); also elsewhere on the board
/Fast_Pulse_ID_P: U25.D7 (DO+); also elsewhere on the board
Clk_40MHz: U24.88 (IO/CLK2p); also elsewhere on the board
GND: C75.1, C76.1, C77.2, C78.2, C79.2, C80.1, J14.2, J14.10, R48.2, R50.1, R54.1, U22.4 (VSS), U22.9 (PAD), U23.1 (GND), U23.7 (GND), U24.121 (DEV_CLRn), U25.B3 (SYNC2); also elsewhere on the board
unnamed: J14.1, R48.1, U24.18 (TCK)
unnamed: J14.3, U24.20 (TDO)
unnamed: J14.5, R49.2, U24.16 (TMS)
unnamed: J14.9, R47.2, U24.19 (TDI)
unnamed: R50.2, U24.15 (JTAGEN)
unnamed: R51.2, U24.136 (nSTATUS)
unnamed: R52.2, U24.138 (CONF_DONE)
unnamed: R53.2, U24.129 (nCONFIG)
unnamed: R54.2, U24.126 (CONFIG_SEL)

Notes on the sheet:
Programming
FPGA -> Serializer 40MHz Clock -> FPGA
Test Point
LVCD -> LVTTL (for now)
MRAM
Clock -> FPGA

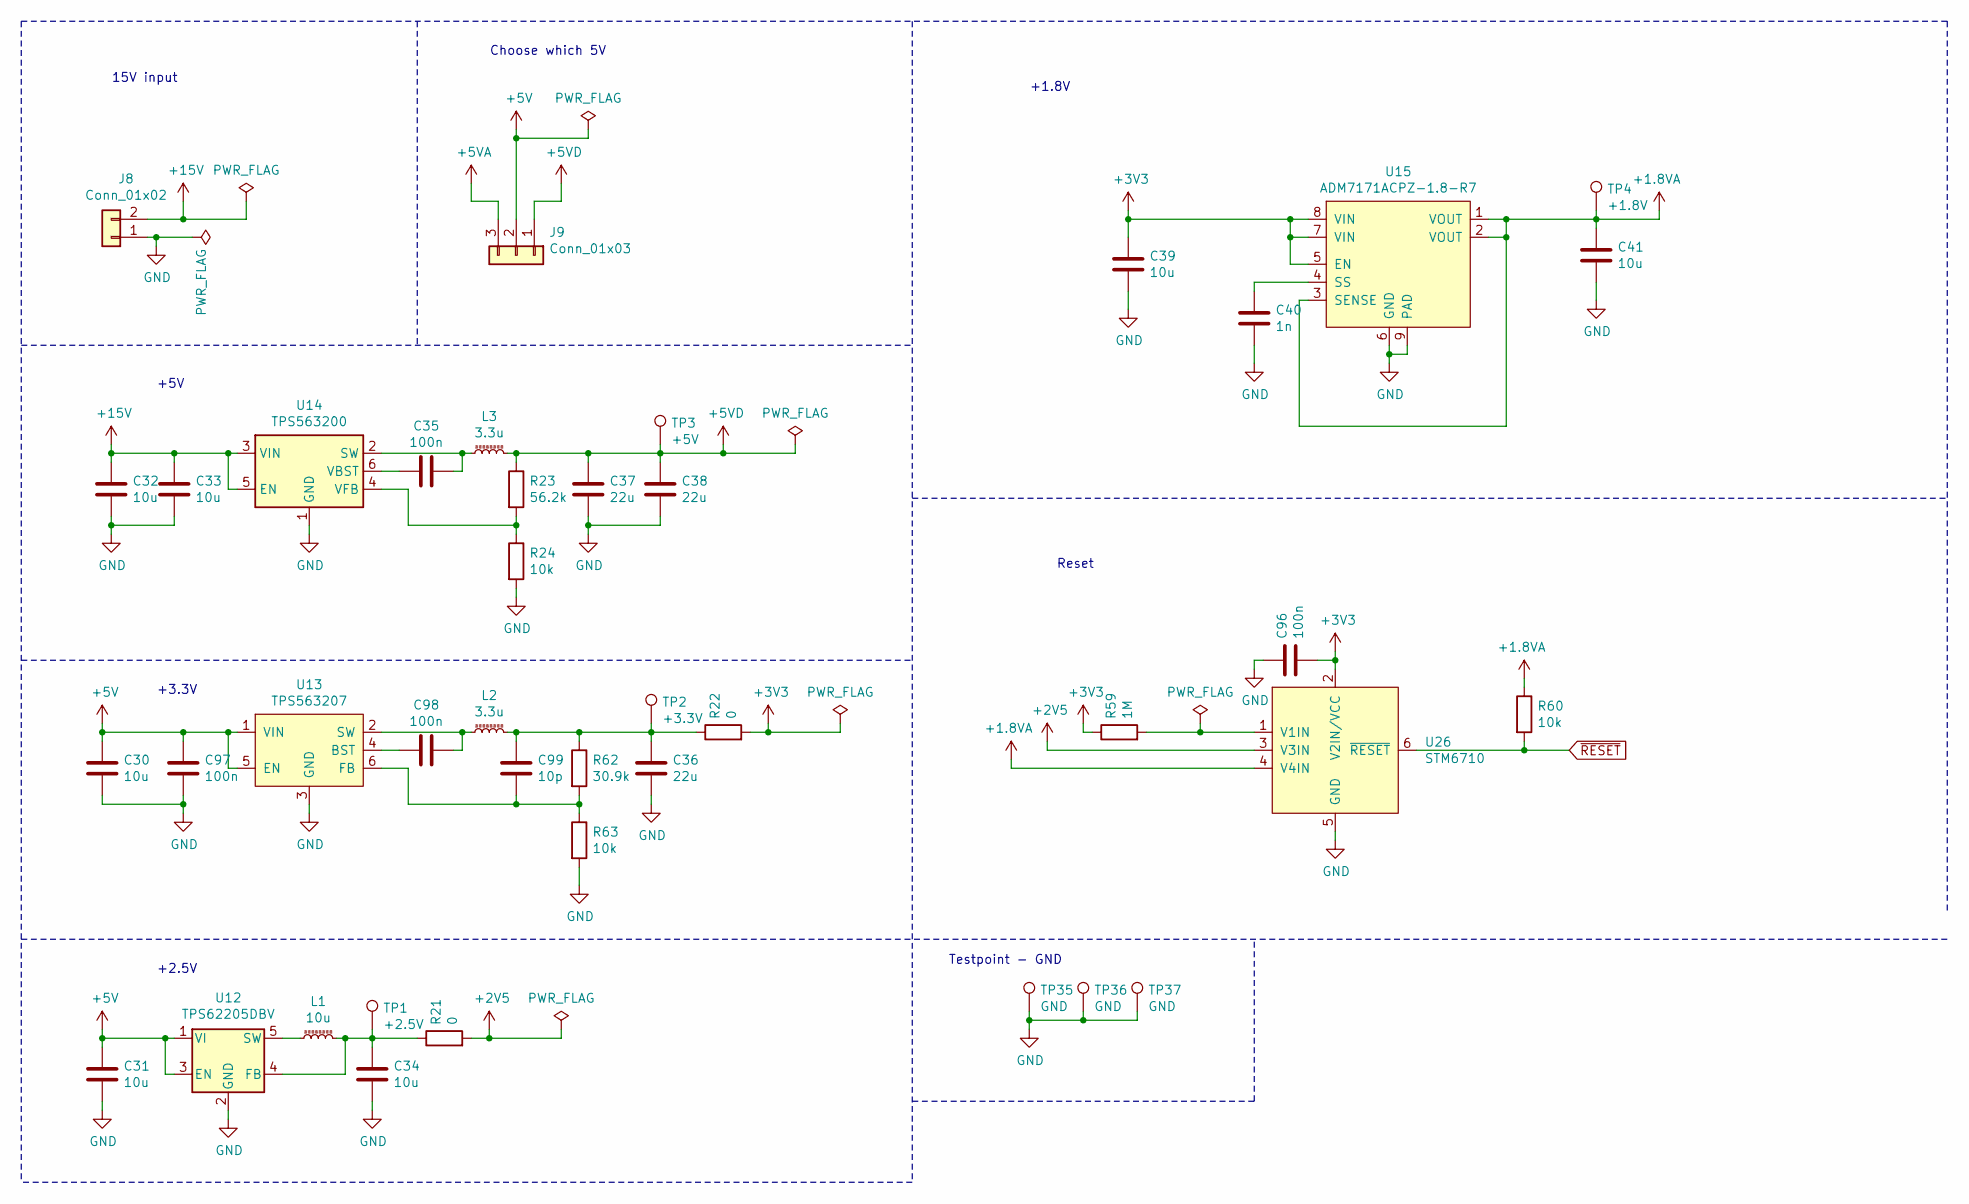
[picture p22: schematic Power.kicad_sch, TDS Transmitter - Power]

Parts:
C30, C31, C32, C33, C34, C39, C41: 10u; C_0603_1608Metric
C35, C96, C97, C98: 100n; C_0603_1608Metric
C36, C37, C38: 22u; C_0603_1608Metric
C40: 1n; C_0603_1608Metric
C99: 10p; C_0603_1608Metric
J8: Conn_01x02; 3.81mm_2_pos
J9: Conn_01x03; PinHeader_1x03_P2.54mm_Vertical
L1: 10u; L_1008_2520Metric
L2, L3: 3.3u; L_Bourns-SRN8040_8x8.15mm
R21: 0; R_0603_1608Metric
R22: 0; R_1206_3216Metric
R23: 56.2k; R_0603_1608Metric
R24, R60, R63: 10k; R_0603_1608Metric
R59: 1M; R_0603_1608Metric
R62: 30.9k; R_0603_1608Metric
TP1: +2.5V; TestPoint_THTPad_D1.5mm_Drill0.7mm
TP2: +3.3V; TestPoint_THTPad_D1.5mm_Drill0.7mm
TP3: +5V; TestPoint_THTPad_D1.5mm_Drill0.7mm
TP4: +1.8V; TestPoint_THTPad_D1.5mm_Drill0.7mm
TP35, TP36, TP37: GND; TestPoint_THTPad_D1.5mm_Drill0.7mm
U12: TPS62205DBV; SOT-23-5
U13: TPS563207; SOT-563
U14: TPS563200; SOT-23-6
U15: ADM7171ACPZ-1.8-R7; LFCSP-8-1EP_3x3mm_P0.5mm_EP1.45x1.74mm
U26: STM6710; SOT-23-6

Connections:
+1V0: C41.1, R60.1, TP4.1, U15.1 (VOUT), U15.2 (VOUT), U15.3 (SENSE), U26.4 (V4IN); also elsewhere on the board
+2V5: R21.2, U26.3 (V3IN); also elsewhere on the board
+3V3: C39.1, C96.2, R22.2, R59.1, U15.5 (EN), U15.7 (VIN), U15.8 (VIN), U26.2 (V2IN/VCC); also elsewhere on the board
+5V: C30.1, C31.1, C97.1, J9.2, U12.1 (VI), U12.3 (EN), U13.1 (VIN), U13.5 (EN)
+5VA: J9.3; also elsewhere on the board
+5VD: C37.1, C38.1, J9.1, L3.2, R23.1, TP3.1
+15V: C32.1, C33.1, J8.2, U14.3 (VIN), U14.5 (EN); also elsewhere on the board
GND: C30.2, C31.2, C32.2, C33.2, C34.2, C36.2, C37.2, C38.2, C39.2, C40.2, C41.2, C96.1, C97.2, J8.1, R24.2, R63.2, TP35.1, TP36.1, TP37.1, U12.2 (GND), U13.3 (GND), U14.1 (GND), U15.6 (GND), U15.9 (PAD), U26.5 (GND); also elsewhere on the board
unnamed: C34.1, L1.2, R21.1, TP1.1, U12.4 (FB)
unnamed: C35.1, L3.1, U14.2 (SW)
unnamed: C35.2, U14.6 (VBST)
unnamed: C36.1, C99.1, L2.2, R22.1, R62.1, TP2.1
unnamed: C40.1, U15.4 (SS)
unnamed: C98.1, L2.1, U13.2 (SW)
unnamed: C98.2, U13.4 (BST)
unnamed: C99.2, R62.2, R63.1, U13.6 (FB)
unnamed: L1.1, U12.5 (SW)
unnamed: R23.2, R24.1, U14.4 (VFB)
unnamed: R59.2, U26.1 (V1IN)
~RESET: R60.2, U26.6 (~RESET); also elsewhere on the board

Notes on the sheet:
+2.5V
Testpoint - GND
+5V
+1.8V
Reset
Choose which 5V
15V input
+3.3V

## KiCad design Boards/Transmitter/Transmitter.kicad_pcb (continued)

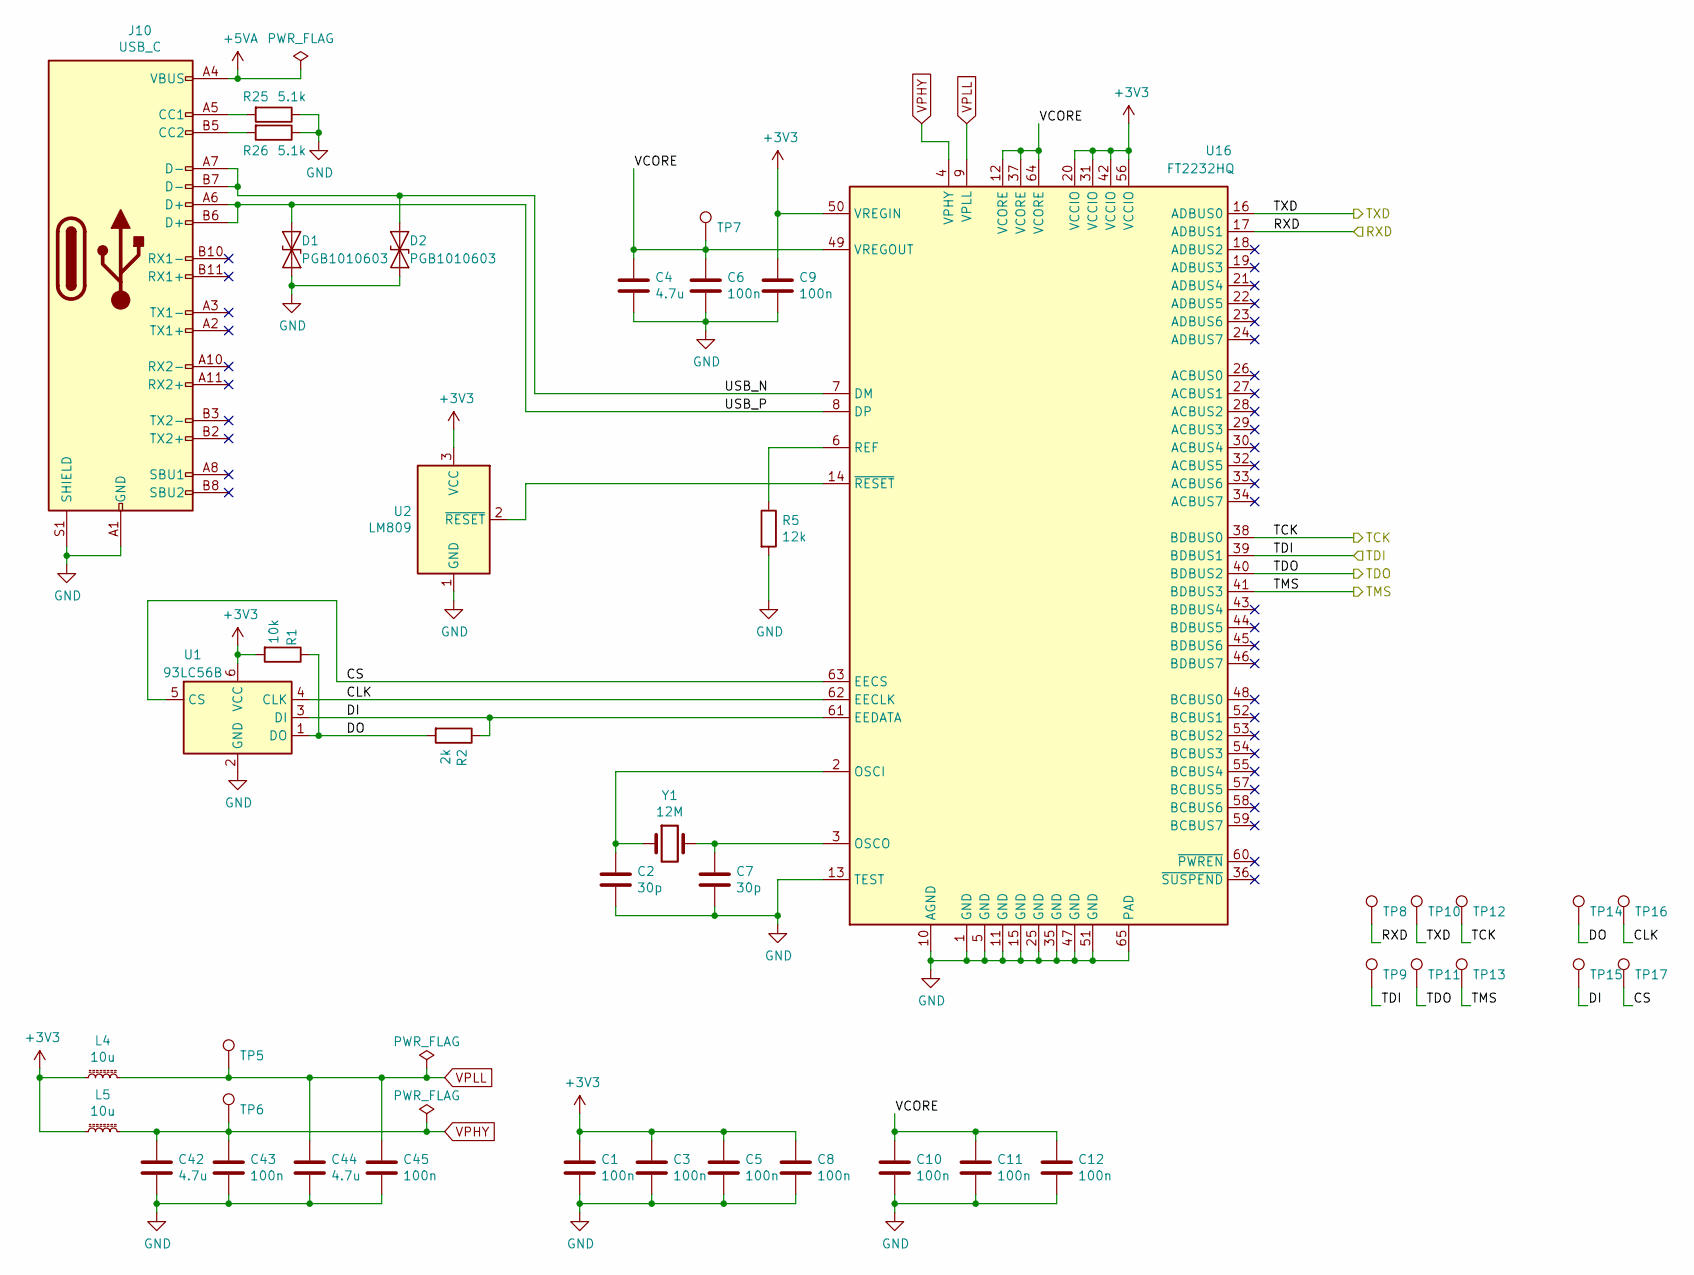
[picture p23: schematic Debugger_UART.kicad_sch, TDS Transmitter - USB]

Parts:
C1, C3, C5, C6, C8, C9, C10, C11, C12, C43, C45: 100n; C_0603_1608Metric
C2, C7: 30p; C_0603_1608Metric
C4, C42, C44: 4.7u; C_0603_1608Metric
D1, D2: PGB1010603; D_0603_1608Metric
J10: USB_C; USB_C_Receptacle_Amphenol_12401610E4-2A_CircularHoles
L4, L5: 10u; L_1008_2520Metric
R1: 10k; R_0603_1608Metric
R2: 2k; R_0603_1608Metric
R5: 12k; R_0603_1608Metric
R25, R26: 5.1k; R_0603_1608Metric
TP5, TP6, TP7, TP8, TP9, TP10, TP11, TP12, TP13, TP14, TP15, TP16, TP17: TestPoint; TestPoint_THTPad_D1.5mm_Drill0.7mm
U1: 93LC56B; SOT-23-6
U2: LM809; SOT-23
U16: FT2232HQ; QFN-64-1EP_9x9mm_P0.5mm_EP4.35x4.35mm
Y1: 12M; Crystal_SMD_5032-2Pin_5.0x3.2mm

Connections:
+3V3: C1.1, C3.1, C5.1, C8.1, C9.1, L4.1, L5.1, R1.2, U1.6 (VCC), U2.3 (VCC), U16.20 (VCCIO), U16.31 (VCCIO), U16.42 (VCCIO), U16.50 (VREGIN), U16.56 (VCCIO); also elsewhere on the board
+5VA: J10.A4 (VBUS), J10.A9 (VBUS), J10.B4 (VBUS), J10.B9 (VBUS); also elsewhere on the board
/Debugger_UART/CLK: TP16.1, U1.4 (CLK), U16.62 (EECLK)
/Debugger_UART/CS: TP17.1, U1.5 (CS), U16.63 (EECS)
/Debugger_UART/DI: R2.1, TP15.1, U1.3 (DI), U16.61 (EEDATA)
/Debugger_UART/DO: R1.1, R2.2, TP14.1, U1.1 (DO)
/Debugger_UART/RXD: TP8.1, U16.17 (ADBUS1); also elsewhere on the board
/Debugger_UART/TCK: TP12.1, U16.38 (BDBUS0); also elsewhere on the board
/Debugger_UART/TDI: TP9.1, U16.39 (BDBUS1); also elsewhere on the board
/Debugger_UART/TDO: TP11.1, U16.40 (BDBUS2); also elsewhere on the board
/Debugger_UART/TMS: TP13.1, U16.41 (BDBUS3); also elsewhere on the board
/Debugger_UART/USB_N: D2.1 (A1), J10.A7 (D-), J10.B7 (D-), U16.7 (DM)
/Debugger_UART/USB_P: D1.1 (A1), J10.A6 (D+), J10.B6 (D+), U16.8 (DP)
/Debugger_UART/VCORE: C4.1, C6.1, C10.1, C11.1, C12.1, TP7.1, U16.12 (VCORE), U16.37 (VCORE), U16.49 (VREGOUT), U16.64 (VCORE)
/FPGA_MRAM_Serializer/RXD: TP10.1, U16.16 (ADBUS0); also elsewhere on the board
GND: C1.2, C2.2, C3.2, C4.2, C5.2, C6.2, C7.2, C8.2, C9.2, C10.2, C11.2, C12.2, C42.2, C43.2, C44.2, C45.2, D1.2 (A2), D2.2 (A2), J10.A1 (GND), J10.A12 (GND), J10.B1 (GND), J10.B12 (GND), J10.S1 (SHIELD), R5.2, R25.1, R26.1, U1.2 (GND), U2.1 (GND), U16.1 (GND), U16.5 (GND), U16.10 (AGND), U16.11 (GND), U16.13 (TEST), U16.15 (GND), U16.25 (GND), U16.35 (GND), U16.47 (GND), U16.51 (GND), U16.65 (PAD); also elsewhere on the board
unnamed: C2.1, U16.2 (OSCI), Y1.1
unnamed: C7.1, U16.3 (OSCO), Y1.2
unnamed: J10.A5 (CC1), R25.2
unnamed: J10.B5 (CC2), R26.2
unnamed: R5.1, U16.6 (REF)
unnamed: U2.2 (~RESET), U16.14 (~RESET)
VPHY: C42.1, C43.1, L5.2, TP6.1, U16.4 (VPHY)
VPLL: C44.1, C45.1, L4.2, TP5.1, U16.9 (VPLL)

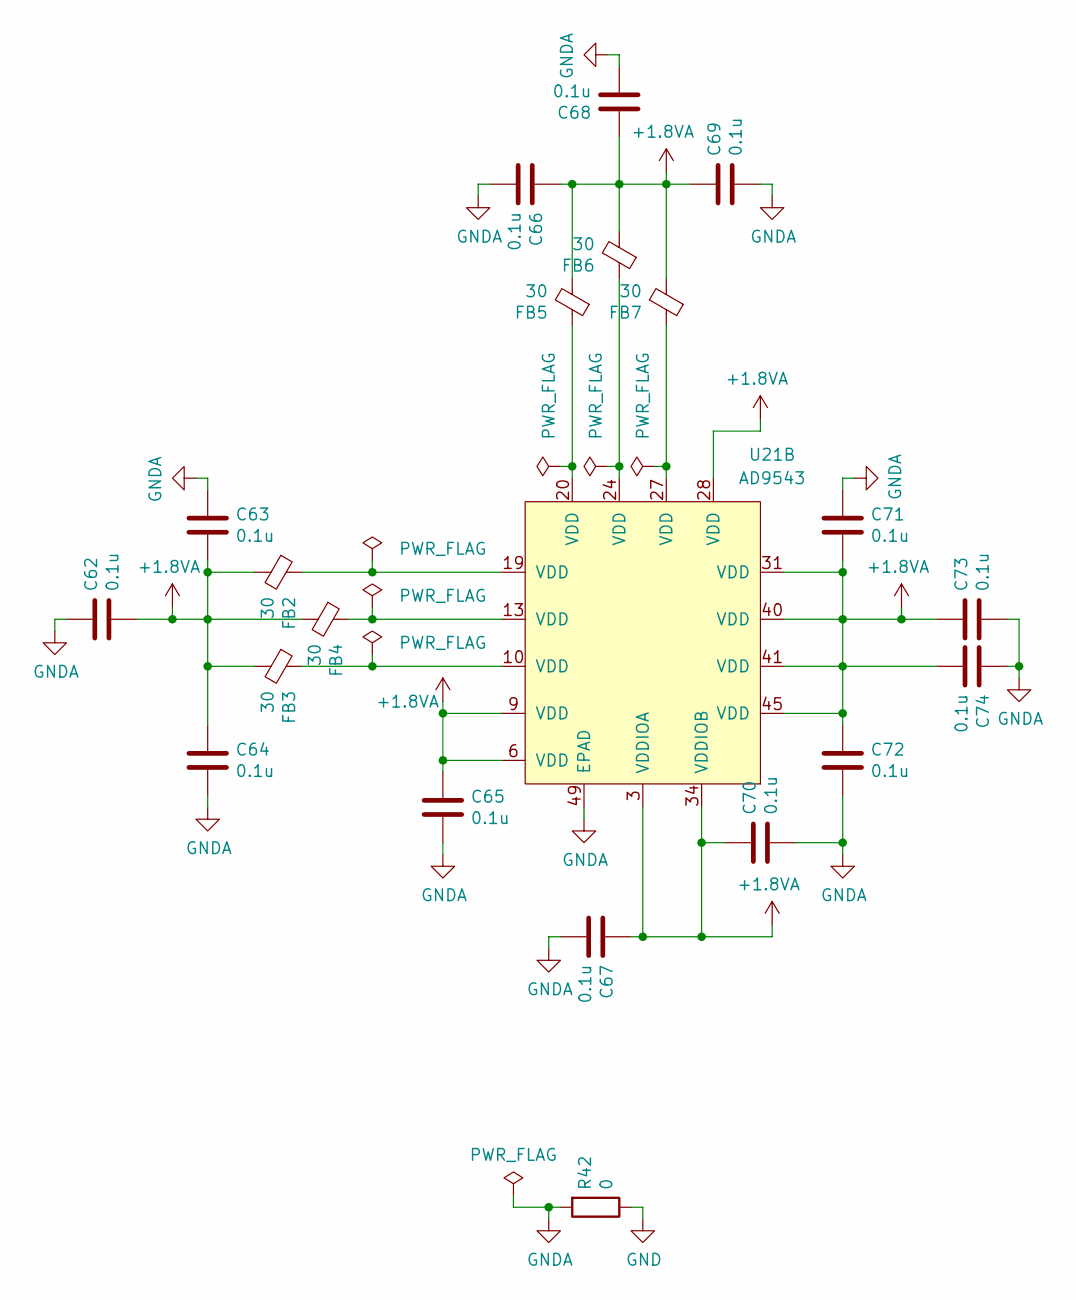
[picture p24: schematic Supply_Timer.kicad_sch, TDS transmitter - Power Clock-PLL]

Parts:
C62, C63, C64, C65, C66, C67, C68, C69, C70, C71, C72, C73, C74: 0.1u; C_0402_1005Metric
FB2, FB3, FB4, FB5, FB6, FB7: 30; L_0402_1005Metric
R42: 0; R_0603_1608Metric
U21: AD9543; LFCSP-48-1EP_7x7mm_P0.5mm_EP4.1x4.1mm

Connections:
+1V0: C62.1, C63.1, C64.2, C65.2, C66.2, C67.2, C68.2, C69.2, C70.2, C71.1, C72.2, C73.2, C74.1, FB2.2, FB3.2, FB4.2, FB5.2, FB6.2, FB7.2, U21.3 (VDDIOA), U21.6 (VDD), U21.9 (VDD), U21.28 (VDD), U21.31 (VDD), U21.34 (VDDIOB), U21.40 (VDD), U21.41 (VDD), U21.45 (VDD); also elsewhere on the board
GND: R42.1; also elsewhere on the board
GNDA: C62.2, C63.2, C64.1, C65.1, C66.1, C67.1, C68.1, C69.1, C70.1, C71.2, C72.1, C73.1, C74.2, R42.2, U21.49 (EPAD); also elsewhere on the board
unnamed: FB2.1, U21.19 (VDD)
unnamed: FB3.1, U21.10 (VDD)
unnamed: FB4.1, U21.13 (VDD)
unnamed: FB5.1, U21.20 (VDD)
unnamed: FB6.1, U21.24 (VDD)
unnamed: FB7.1, U21.27 (VDD)

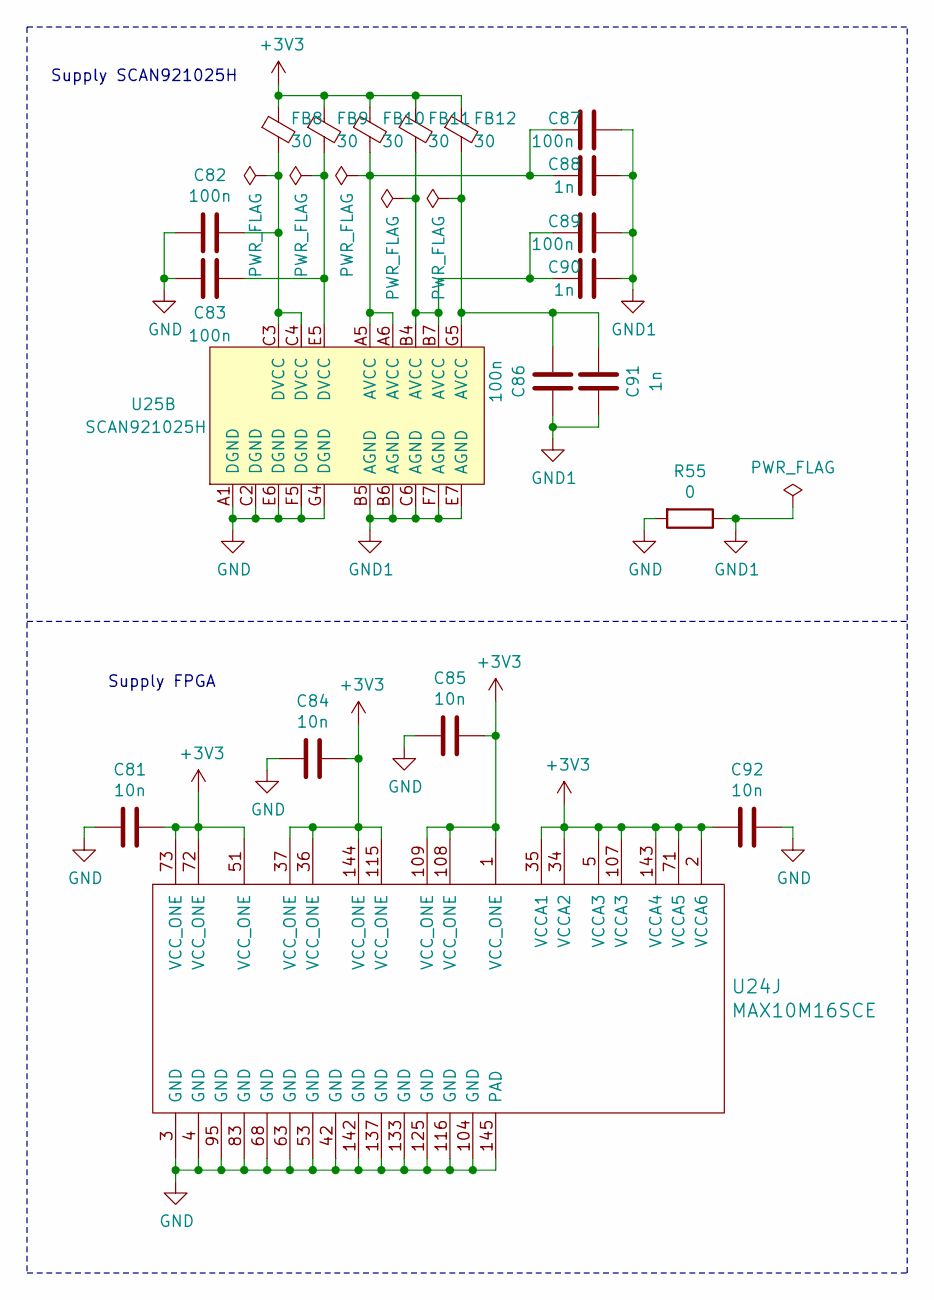
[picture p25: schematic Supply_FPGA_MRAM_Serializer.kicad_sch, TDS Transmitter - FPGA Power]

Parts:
C81, C84, C85, C92: 10n; C_0603_1608Metric
C82, C83, C86, C87, C89: 100n; C_0402_1005Metric
C88, C90, C91: 1n; C_0402_1005Metric
FB8, FB9, FB10, FB11, FB12: 30; L_0402_1005Metric
R55: 0; R_0603_1608Metric
U24: MAX10M16SCE; EQFP_144
U25: SCAN921025H; BGA-49_7x7_7.0x7.0mm

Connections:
+3V3: C81.1, C84.1, C85.1, C92.2, FB8.1, FB9.1, FB10.1, FB11.1, FB12.1, U24.1 (VCC_ONE), U24.2 (VCCA6), U24.5 (VCCA3), U24.34 (VCCA2), U24.35 (VCCA1), U24.36 (VCC_ONE), U24.37 (VCC_ONE), U24.51 (VCC_ONE), U24.71 (VCCA5), U24.72 (VCC_ONE), U24.73 (VCC_ONE), U24.107 (VCCA3), U24.108 (VCC_ONE), U24.109 (VCC_ONE), U24.115 (VCC_ONE), U24.143 (VCCA4), U24.144 (VCC_ONE); also elsewhere on the board
GND: C81.2, C82.2, C83.2, C84.2, C85.2, C92.1, R55.2, U24.3 (GND), U24.4 (GND), U24.42 (GND), U24.53 (GND), U24.63 (GND), U24.68 (GND), U24.83 (GND), U24.95 (GND), U24.104 (GND), U24.116 (GND), U24.125 (GND), U24.133 (GND), U24.137 (GND), U24.142 (GND), U24.145 (PAD), U25.A1 (DGND), U25.C2 (DGND), U25.E6 (DGND), U25.F5 (DGND), U25.G4 (DGND); also elsewhere on the board
GND1: C86.1, C87.2, C88.1, C89.2, C90.2, C91.2, R55.1, U25.B5 (AGND), U25.B6 (AGND), U25.C6 (AGND), U25.E7 (AGND), U25.F7 (AGND)
unnamed: C82.1, FB8.2, U25.C3 (DVCC), U25.C4 (DVCC)
unnamed: C83.1, FB9.2, U25.E5 (DVCC)
unnamed: C86.2, C91.1, FB12.2, U25.G5 (AVCC)
unnamed: C87.1, C88.2, FB10.2, U25.A5 (AVCC), U25.A6 (AVCC)
unnamed: C89.1, C90.1, FB11.2, U25.B4 (AVCC), U25.B7 (AVCC)

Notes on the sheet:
Supply FPGA
Supply SCAN921025H

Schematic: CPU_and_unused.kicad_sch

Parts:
C52, C93, C94, C95: 100n; C_0603_1608Metric
FB13: 30; L_0402_1005Metric
J15: Conn_01x14; PinHeader_1x14_P2.54mm_Vertical
J16: LED_1; 3.81mm_2_pos
J17: LED_2; 3.81mm_2_pos
J18: LED_3; 3.81mm_2_pos
Q1, Q2, Q3: BSS123; SOT-23
R56, R57, R58: 0; R_0603_1608Metric
U24: MAX10M16SCE; EQFP_144

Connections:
+1V0: FB13.1; also elsewhere on the board
+3V3: C93.1, C94.2, C95.1, J15.1, R56.1, R57.1, R58.1, U24.9 (VCCIO1A), U24.23 (VCCIO1B), U24.40 (VCCIO3), U24.49 (VCCIO3), U24.117 (VCCIO7), U24.128 (VCCIO8), U24.139 (VCCIO8); also elsewhere on the board
/Clock/M0: U24.85 (IO); also elsewhere on the board
/Clock/M1: U24.81 (IO); also elsewhere on the board
/Clock/M2: U24.78 (IO); also elsewhere on the board
/Debugger_UART/RXD: U24.39 (IO); also elsewhere on the board
/Debugger_UART/TCK: U24.46 (IO); also elsewhere on the board
/Debugger_UART/TDI: U24.45 (IO); also elsewhere on the board
/Debugger_UART/TDO: U24.44 (IO); also elsewhere on the board
/Debugger_UART/TMS: U24.43 (IO); also elsewhere on the board
/FPGA_MRAM_Serializer/CPU_and_unused/LED_1: Q1.1 (G), U24.50 (IO)
/FPGA_MRAM_Serializer/CPU_and_unused/LED_2: Q2.1 (G), U24.52 (IO)
/FPGA_MRAM_Serializer/CPU_and_unused/LED_3: Q3.1 (G), U24.54 (IO)
/FPGA_MRAM_Serializer/RXD: U24.38 (IO); also elsewhere on the board
/FPGA_MRAM_Serializer/SPI_Timer_CSB: U24.77 (IO/RDN); also elsewhere on the board
/FPGA_MRAM_Serializer/SPI_Timer_SCLK: U24.75 (IO/RUP); also elsewhere on the board
/FPGA_MRAM_Serializer/SPI_Timer_SDIO: U24.76 (IO); also elsewhere on the board
/FPGA_MRAM_Serializer/SPI_Timer_SDO: U24.74 (IO); also elsewhere on the board
/Slow_Pulse_ID: U24.60 (IO); also elsewhere on the board
GND: C52.2, C93.2, C94.1, C95.2, J15.14, Q1.2 (S), Q2.2 (S), Q3.2 (S); also elsewhere on the board
unnamed: C52.1, FB13.2, U24.82 (VCCIO5)
unnamed: J15.2, U24.114 (IO)
unnamed: J15.3, U24.118 (IO)
unnamed: J15.4, U24.119 (IO)
unnamed: J15.5, U24.120 (IO)
unnamed: J15.6, U24.124 (IO)
unnamed: J15.7, U24.127 (IO)
unnamed: J15.8, U24.130 (IO)
unnamed: J15.9, U24.131 (IO)
unnamed: J15.10, U24.132 (IO)
unnamed: J15.11, U24.135 (IO)
unnamed: J15.12, U24.140 (IO)
unnamed: J15.13, U24.141 (IO)
unnamed: J16.1, R56.2
unnamed: J16.2, Q1.3 (D)
unnamed: J17.1, R57.2
unnamed: J17.2, Q2.3 (D)
unnamed: J18.1, R58.2
unnamed: J18.2, Q3.3 (D)
~RESET: U24.86 (IO); also elsewhere on the board

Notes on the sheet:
AD9543 connections Reset recieve
CPU connection
2-3 LEDs herausführen und allgemein noch pins vom fpga ausführen

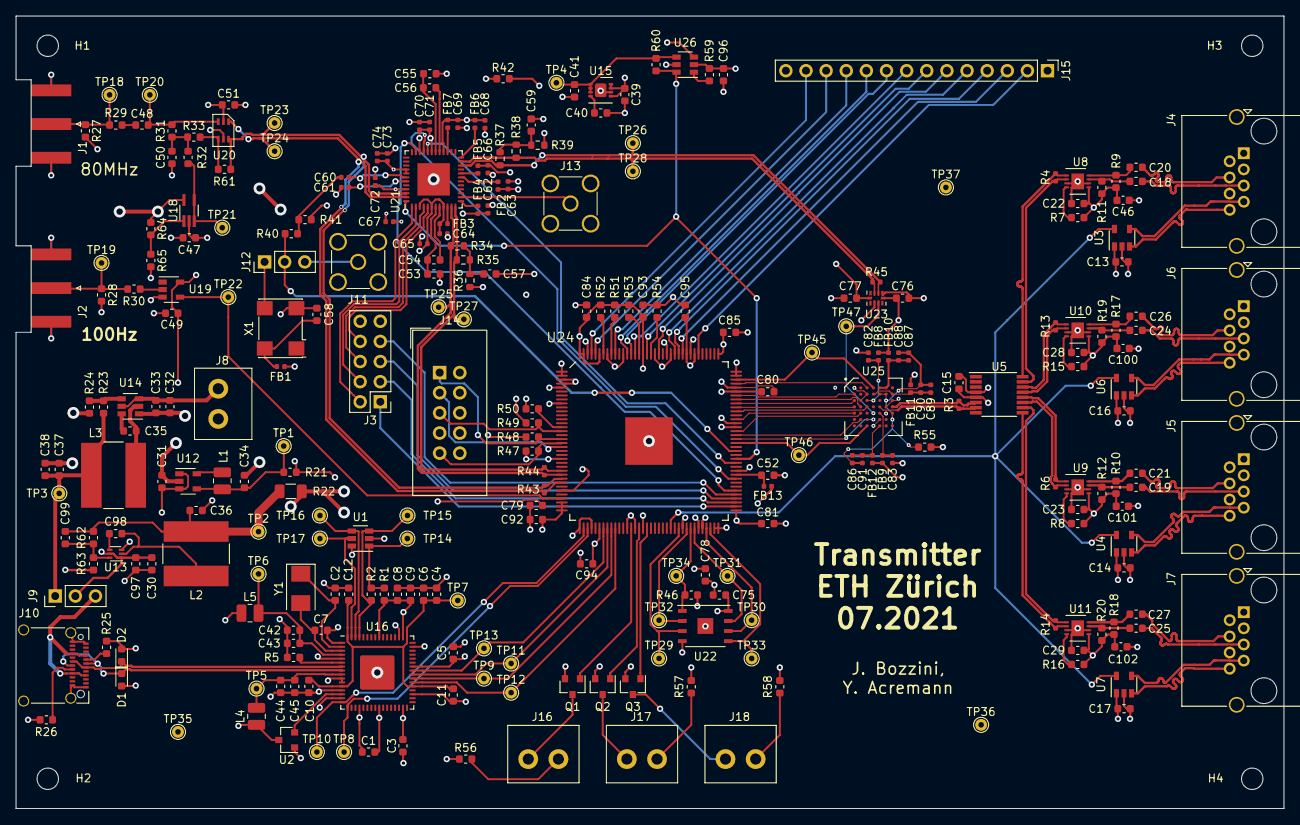
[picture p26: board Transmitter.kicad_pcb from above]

Board: 4 copper layers, 160.0 x 100.0 mm, 279 parts (0 on the bottom side), 184 nets.

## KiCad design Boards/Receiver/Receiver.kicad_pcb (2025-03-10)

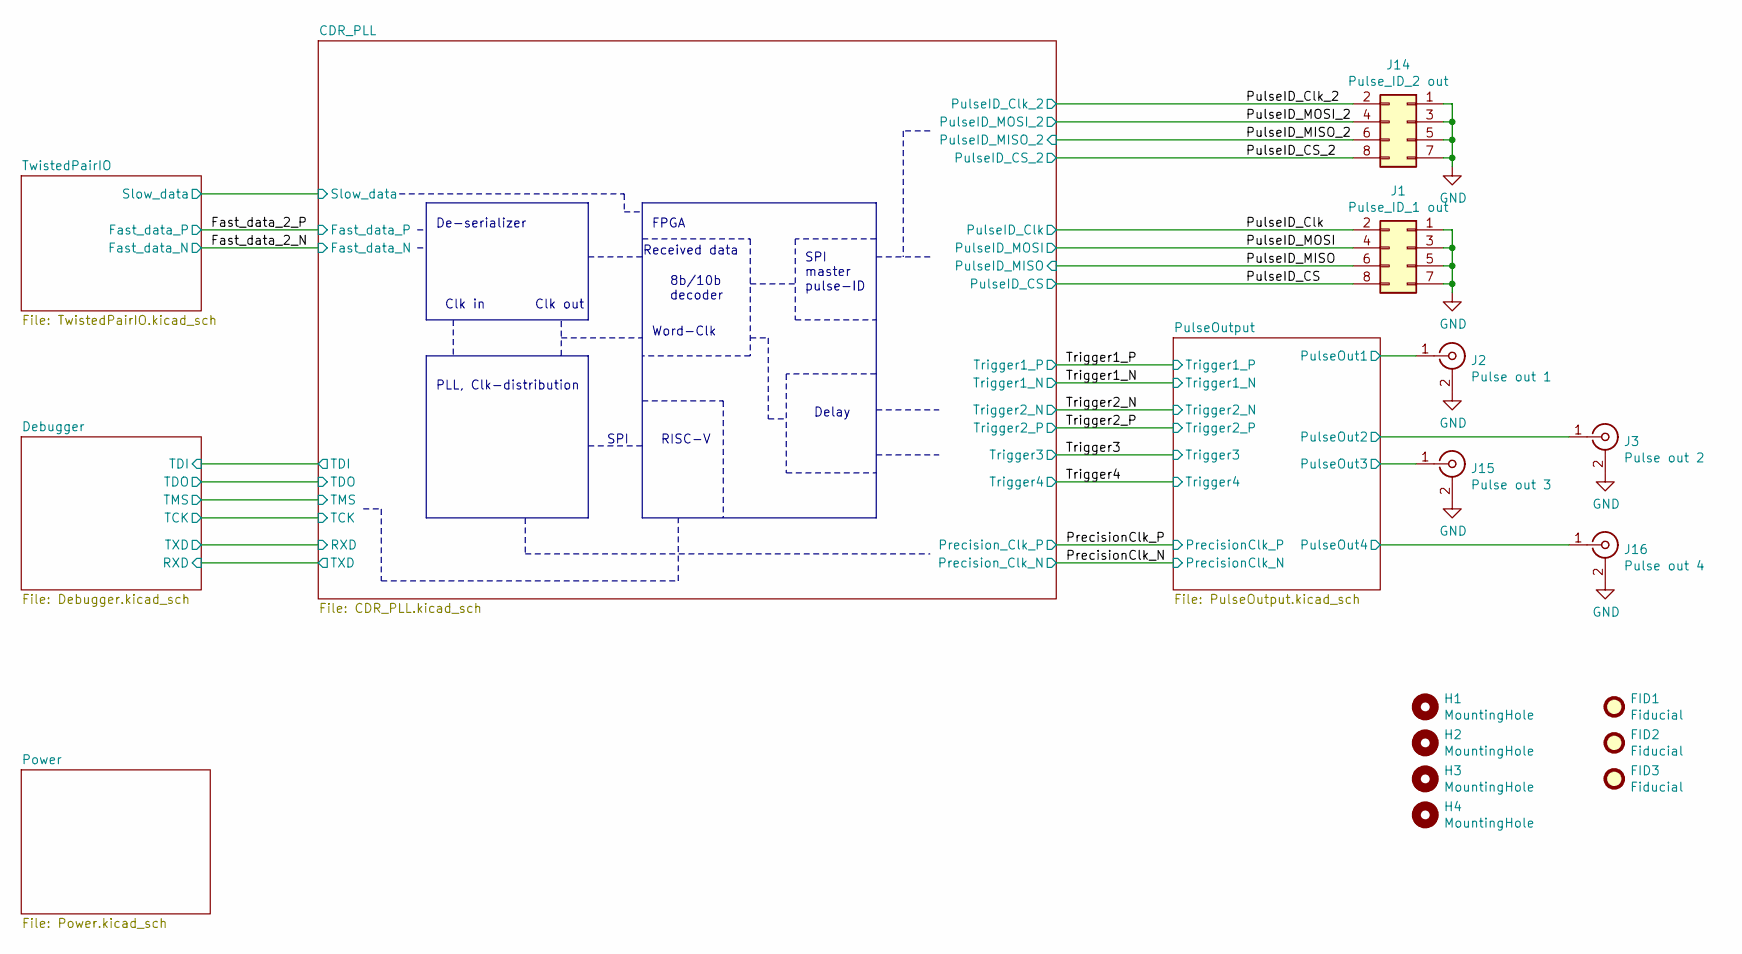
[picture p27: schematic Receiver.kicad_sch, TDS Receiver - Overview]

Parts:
FID1, FID2, FID3: Fiducial; Fiducial_0.5mm_Mask1.5mm
H1, H2, H3, H4: MountingHole; MountingHole_2.7mm_M2.5
J1: Pulse_ID_1 out; PinHeader_2x04_P2.54mm_Vertical
J2: Pulse out 1; SMA_Amphenol_132289_EdgeMount
J3: Pulse out 2; SMA_Amphenol_132289_EdgeMount
J14: Pulse_ID_2 out; PinHeader_2x04_P2.54mm_Vertical
J15: Pulse out 3; SMA_Amphenol_132289_EdgeMount
J16: Pulse out 4; SMA_Amphenol_132289_EdgeMount

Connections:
/PulseID_CS: J1.8; also elsewhere on the board
/PulseID_CS_2: J14.8; also elsewhere on the board
/PulseID_Clk: J1.2; also elsewhere on the board
/PulseID_Clk_2: J14.2; also elsewhere on the board
/PulseID_MISO: J1.6; also elsewhere on the board
/PulseID_MISO_2: J14.6; also elsewhere on the board
/PulseID_MOSI: J1.4; also elsewhere on the board
/PulseID_MOSI_2: J14.4; also elsewhere on the board
/PulseOutput/PulseOut1: J2.1 (In); also elsewhere on the board
/PulseOutput/PulseOut2: J3.1 (In); also elsewhere on the board
/PulseOutput/PulseOut3: J15.1 (In); also elsewhere on the board
/PulseOutput/PulseOut4: J16.1 (In); also elsewhere on the board
GND: J1.1, J1.3, J1.5, J1.7, J2.2 (Ext), J3.2 (Ext), J14.1, J14.3, J14.5, J14.7, J15.2 (Ext), J16.2 (Ext); also elsewhere on the board

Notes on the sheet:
Clk in
SPI master pulse-ID
De-serializer
Delay
8b/10b decoder
PLL, Clk-distribution
Word-Clk
SPI
Received data
Clk out
RISC-V
FPGA

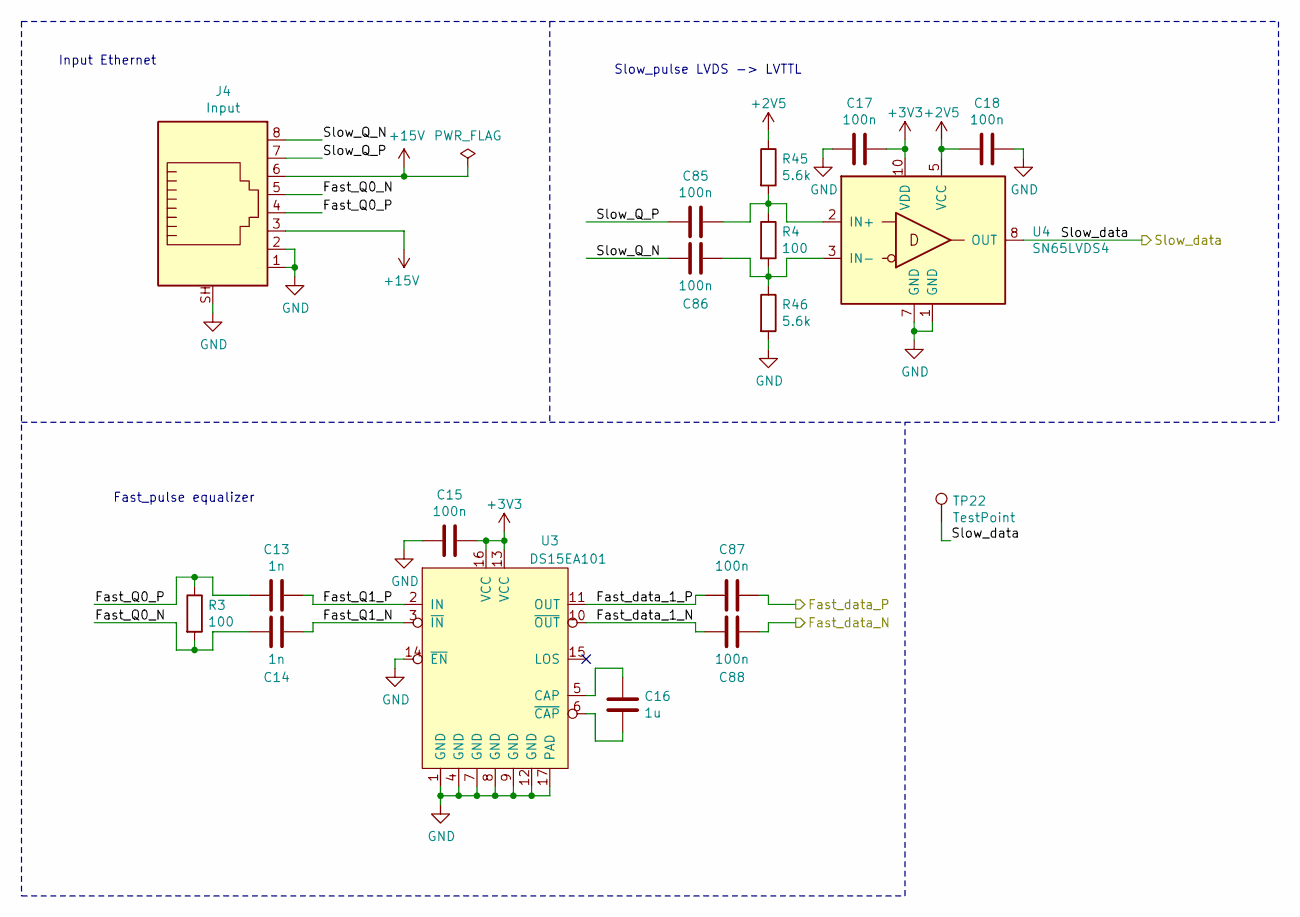
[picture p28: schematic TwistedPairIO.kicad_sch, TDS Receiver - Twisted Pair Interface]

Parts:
C13, C14: 1n; C_0402_1005Metric
C15, C17, C18: 100n; C_0603_1608Metric
C16: 1u; C_0603_1608Metric
C85, C86, C87, C88: 100n; C_0402_1005Metric
J4: Input; RJ45_Amphenol_RJHSE5380
R3, R4: 100; R_0603_1608Metric
R45, R46: 5.6k; R_0603_1608Metric
TP22: TestPoint; TestPoint_THTPad_D1.5mm_Drill0.7mm
U3: DS15EA101; WQFN-16-1EP_4x4mm_P0.5mm_EP2.6x2.6mm
U4: SN65LVDS4; Texas_R-PUQFN-N10

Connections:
+2V5: C18.2, R45.1, U4.5 (VCC); also elsewhere on the board
+3V3: C15.1, C17.1, U3.13 (VCC), U3.16 (VCC), U4.10 (VDD); also elsewhere on the board
+15V: J4.3, J4.6; also elsewhere on the board
/CDR_PLL/Slow_data: TP22.1, U4.8 (OUT); also elsewhere on the board
/Fast_data_2_N: C88.1; also elsewhere on the board
/Fast_data_2_P: C87.1; also elsewhere on the board
/TwistedPairIO/Fast_Q0_N: C14.1, J4.5, R3.2
/TwistedPairIO/Fast_Q0_P: C13.2, J4.4, R3.1
/TwistedPairIO/Fast_Q1_N: C14.2, U3.3 (~IN)
/TwistedPairIO/Fast_Q1_P: C13.1, U3.2 (IN)
/TwistedPairIO/Fast_data_1_N: C88.2, U3.10 (~OUT)
/TwistedPairIO/Fast_data_1_P: C87.2, U3.11 (OUT)
/TwistedPairIO/Slow_Q_N: C86.2, J4.8
/TwistedPairIO/Slow_Q_P: C85.2, J4.7
GND: C15.2, C17.2, C18.1, J4.1, J4.2, J4.SH, R46.2, U3.1 (GND), U3.4 (GND), U3.7 (GND), U3.8 (GND), U3.9 (GND), U3.12 (GND), U3.14 (~EN), U3.17 (PAD), U4.1 (GND), U4.7 (GND); also elsewhere on the board
unnamed: C16.1, U3.5 (CAP)
unnamed: C16.2, U3.6 (~CAP)
unnamed: C85.1, R4.1, R45.2, U4.2 (IN+)
unnamed: C86.1, R4.2, R46.1, U4.3 (IN-)

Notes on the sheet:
Input Ethernet
Fast_pulse equalizer
Slow_pulse LVDS -> LVTTL

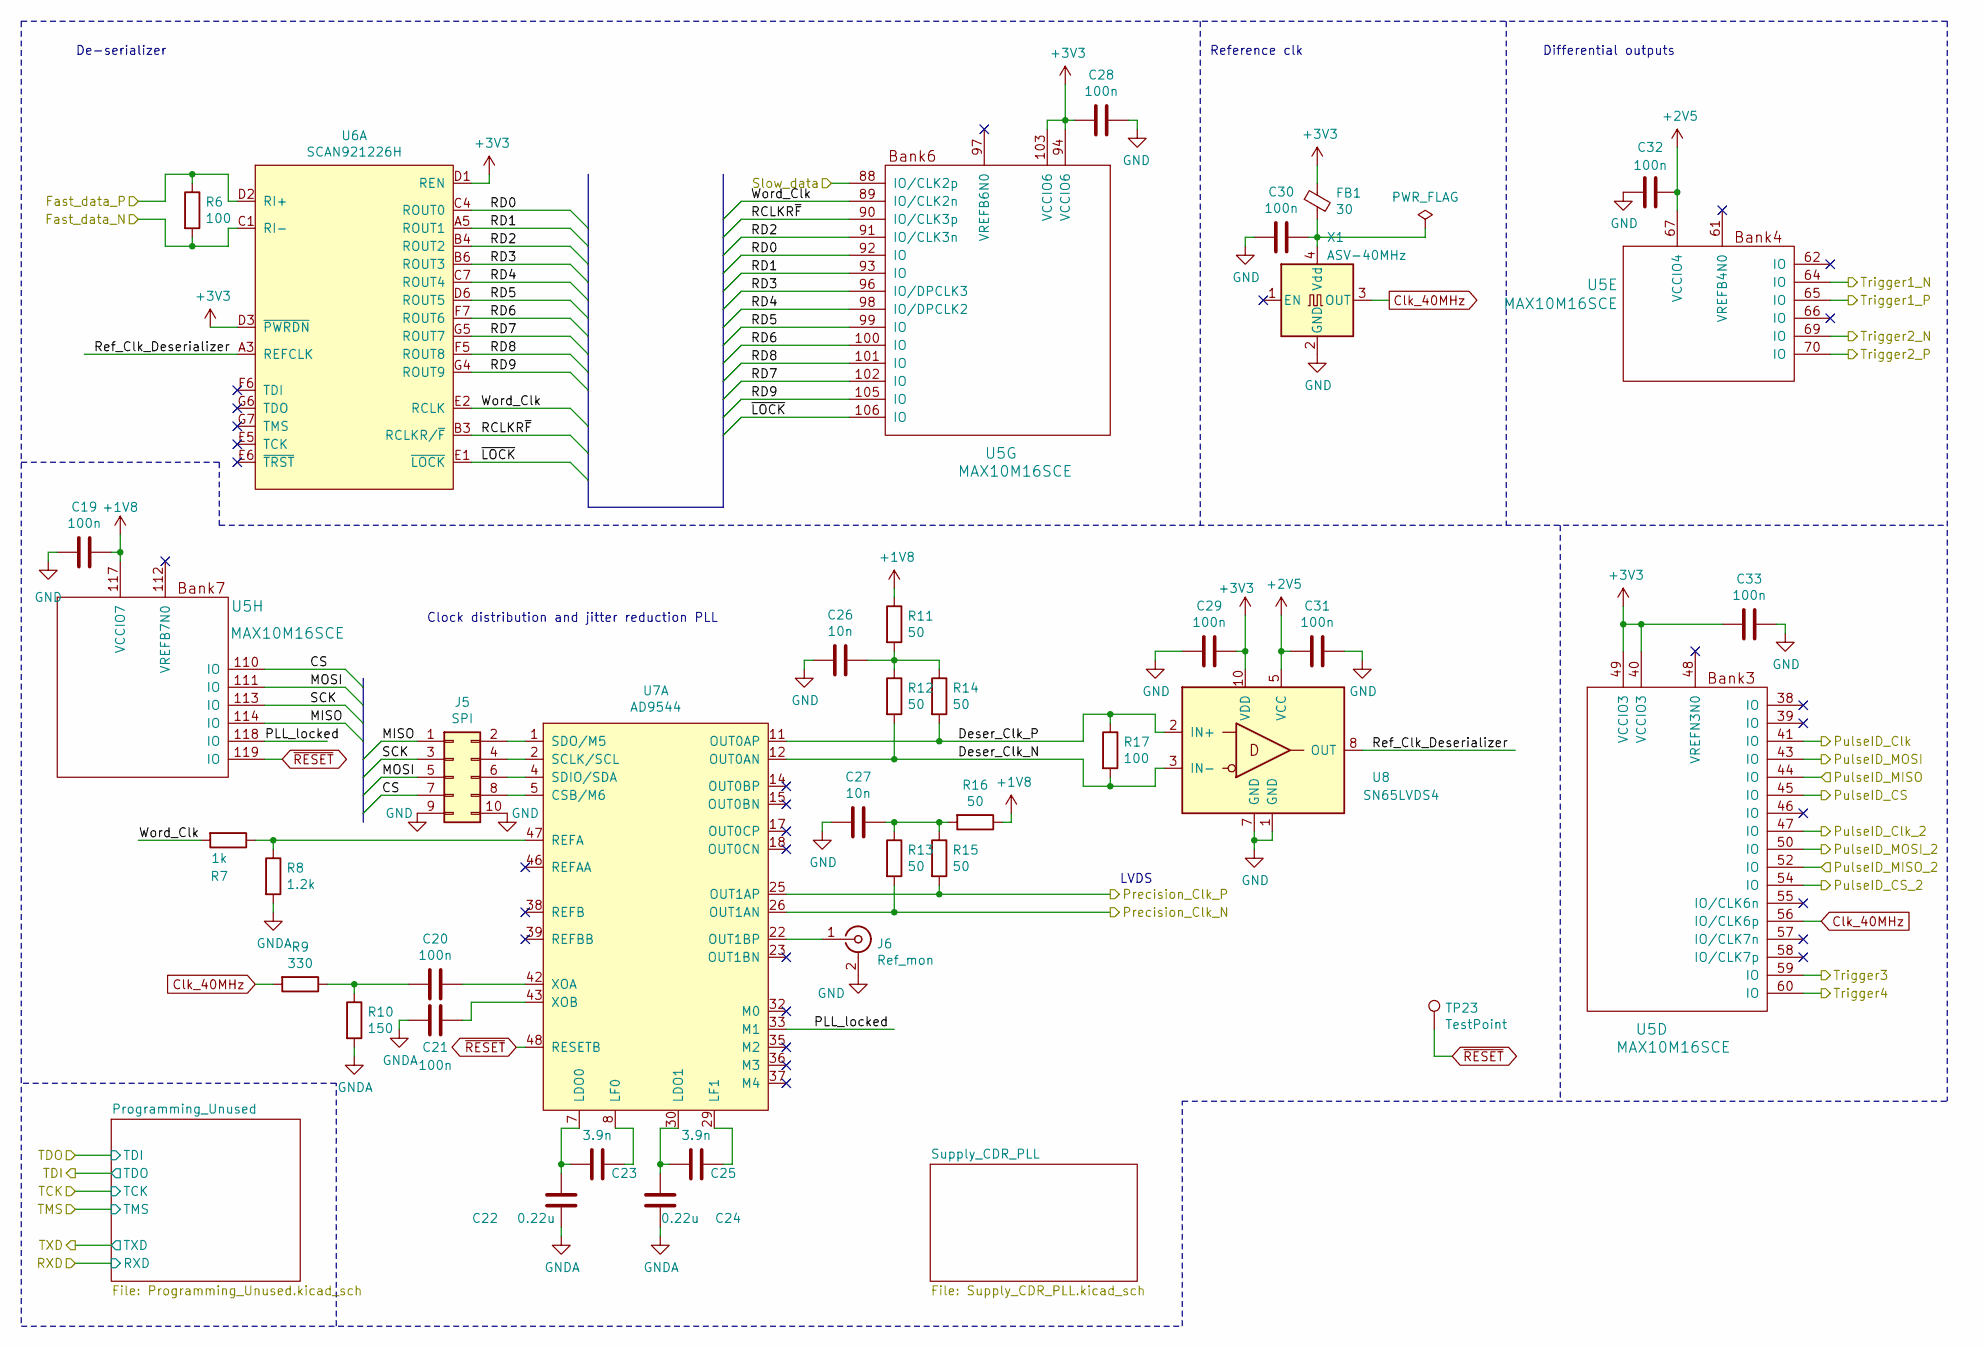
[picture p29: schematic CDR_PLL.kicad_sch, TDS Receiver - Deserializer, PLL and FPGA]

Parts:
C19, C28, C29, C30, C31, C32, C33: 100n; C_0603_1608Metric
C20, C21: 100n; C_0402_1005Metric
C22, C24: 0.22u; C_0603_1608Metric
C23, C25: 3.9n; C_0603_1608Metric
C26, C27: 10n; C_0603_1608Metric
FB1: 30; L_0402_1005Metric
J5: SPI; PinHeader_2x05_P2.54mm_Vertical
J6: Ref_mon; SMA_Amphenol_901-144_Vertical
R6, R17: 100; R_0603_1608Metric
R7: 1k; R_0603_1608Metric
R8: 1.2k; R_0603_1608Metric
R9: 330; R_0603_1608Metric
R10: 150; R_0603_1608Metric
R11, R12, R13, R14, R15, R16: 50; R_0603_1608Metric
TP23: TestPoint; TestPoint_THTPad_D1.5mm_Drill0.7mm
U5: MAX10M16SCE; EQFP_144
U6: SCAN921226H; BGA-49_7x7_7.0x7.0mm
U7: AD9544; LFCSP-48-1EP_7x7mm_P0.5mm_EP4.1x4.1mm
U8: SN65LVDS4; Texas_R-PUQFN-N10
X1: ASV-40MHz; Oscillator_SMD_Abracon_ASV-4Pin_7.0x5.1mm

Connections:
+1V8: C19.1, R11.1, R16.1, U5.117 (VCCIO7); also elsewhere on the board
+2V5: C31.2, C32.1, U5.67 (VCCIO4), U8.5 (VCC); also elsewhere on the board
+3V3: C28.2, C29.1, C33.2, FB1.1, U5.40 (VCCIO3), U5.49 (VCCIO3), U5.94 (VCCIO6), U5.103 (VCCIO6), U6.D1 (REN), U6.D3 (~PWRDN), U8.10 (VDD); also elsewhere on the board
/CDR_PLL/CS: J5.7, U5.110 (IO)
/CDR_PLL/Deser_Clk_N: R12.2, R17.2, U7.12 (OUT0AN), U8.3 (IN-)
/CDR_PLL/Deser_Clk_P: R14.2, R17.1, U7.11 (OUT0AP), U8.2 (IN+)
/CDR_PLL/MISO: J5.1, U5.114 (IO)
/CDR_PLL/MOSI: J5.5, U5.111 (IO)
/CDR_PLL/PLL_locked: U5.118 (IO), U7.33 (M1)
/CDR_PLL/RCLKR~F: U5.90 (IO/CLK3p), U6.B3 (RCLKR/~F)
/CDR_PLL/RD0: U5.92 (IO), U6.C4 (ROUT0)
/CDR_PLL/RD1: U5.93 (IO), U6.A5 (ROUT1)
/CDR_PLL/RD2: U5.91 (IO/CLK3n), U6.B4 (ROUT2)
/CDR_PLL/RD3: U5.96 (IO/DPCLK3), U6.B6 (ROUT3)
/CDR_PLL/RD4: U5.98 (IO/DPCLK2), U6.C7 (ROUT4)
/CDR_PLL/RD5: U5.99 (IO), U6.D6 (ROUT5)
/CDR_PLL/RD6: U5.100 (IO), U6.F7 (ROUT6)
/CDR_PLL/RD7: U5.102 (IO), U6.G5 (ROUT7)
/CDR_PLL/RD8: U5.101 (IO), U6.F5 (ROUT8)
/CDR_PLL/RD9: U5.105 (IO), U6.G4 (ROUT9)
/CDR_PLL/Ref_Clk_Deserializer: U6.A3 (REFCLK), U8.8 (OUT)
/CDR_PLL/SCK: J5.3, U5.113 (IO)
/CDR_PLL/Slow_data: U5.88 (IO/CLK2p); also elsewhere on the board
/CDR_PLL/Word_Clk: R7.2, U5.89 (IO/CLK2n), U6.E2 (RCLK)
/CDR_PLL/~LOCK: U5.106 (IO), U6.E1 (~LOCK)
/Fast_data_2_N: R6.2, U6.C1 (RI-); also elsewhere on the board
/Fast_data_2_P: R6.1, U6.D2 (RI+); also elsewhere on the board
/PrecisionClk_N: R13.2, U7.26 (OUT1AN); also elsewhere on the board
/PrecisionClk_P: R15.2, U7.25 (OUT1AP); also elsewhere on the board
/PulseID_CS: U5.45 (IO); also elsewhere on the board
/PulseID_CS_2: U5.54 (IO); also elsewhere on the board
/PulseID_Clk: U5.41 (IO); also elsewhere on the board
/PulseID_Clk_2: U5.47 (IO); also elsewhere on the board
/PulseID_MISO: U5.44 (IO); also elsewhere on the board
/PulseID_MISO_2: U5.52 (IO); also elsewhere on the board
/PulseID_MOSI: U5.43 (IO); also elsewhere on the board
/PulseID_MOSI_2: U5.50 (IO); also elsewhere on the board
/Trigger1_N: U5.64 (IO); also elsewhere on the board
/Trigger1_P: U5.65 (IO); also elsewhere on the board
/Trigger2_N: U5.69 (IO); also elsewhere on the board
/Trigger2_P: U5.70 (IO); also elsewhere on the board
/Trigger3: U5.59 (IO); also elsewhere on the board
/Trigger4: U5.60 (IO); also elsewhere on the board
Clk_40MHz: R9.2, U5.56 (IO/CLK6p), X1.3 (OUT); also elsewhere on the board
GND: C19.2, C26.2, C27.2, C28.1, C29.2, C30.2, C31.1, C32.2, C33.1, J5.9, J5.10, J6.2 (Ext), U8.1 (GND), U8.7 (GND), X1.2 (GND); also elsewhere on the board
GNDA: C21.2, C22.2, C24.2, R8.2, R10.2; also elsewhere on the board
unnamed: C20.1, U7.42 (XOA)
unnamed: C20.2, R9.1, R10.1
unnamed: C21.1, U7.43 (XOB)
unnamed: C22.1, C23.2, U7.7 (LDO0)
unnamed: C23.1, U7.8 (LF0)
unnamed: C24.1, C25.2, U7.30 (LDO1)
unnamed: C25.1, U7.29 (LF1)
unnamed: C26.1, R11.2, R12.1, R14.1
unnamed: C27.1, R13.1, R15.1, R16.2
unnamed: C30.1, FB1.2, X1.4 (Vdd)
unnamed: J5.2, U7.1 (SDO/M5)
unnamed: J5.4, U7.2 (SCLK/SCL)
unnamed: J5.6, U7.4 (SDIO/SDA)
unnamed: J5.8, U7.5 (CSB/M6)
unnamed: J6.1 (In), U7.22 (OUT1BP)
unnamed: R7.1, R8.1, U7.47 (REFA)
~RESET: TP23.1, U5.119 (IO), U7.48 (RESETB)

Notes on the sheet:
De-serializer
Clock distribution and jitter reduction PLL
Reference clk
Differential outputs
LVDS

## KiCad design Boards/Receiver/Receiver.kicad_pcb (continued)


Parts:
C64, C65, C66, C67, C68, C69, C89, C90, C91, C92, C93: 100n; C_0603_1608Metric
D3, D4, D6, D7: D_Zener; D_0805_2012Metric
R33, R34, R47: 100; R_0603_1608Metric
R35, R36, R37, R38, R48, R49, R50, R51: 50; R_0603_1608Metric
U9: NB3L8504S; TSSOP-16_4.4x5mm_P0.65mm
U10, U21: NB7V52M; QFN-16-1EP_3x3mm_P0.5mm_EP1.9x1.9mm
U11, U19: SN65LVDS4; Texas_R-PUQFN-N10
U12, U20: 74AUP1G79GW; SOT-353_SC-70-5_Handsoldering
U13, U22: MC100EPT21; TSSOP-8_3x3mm_P0.65mm

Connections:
+2V5: C65.1, C67.2, C90.2, C92.1, R35.1, R36.1, R49.1, R50.1, U10.12 (VCC), U10.15 (~R), U11.5 (VCC), U19.5 (VCC), U21.12 (VCC), U21.15 (~R); also elsewhere on the board
+3V3: C64.1, C66.1, C68.1, C69.1, C89.1, C91.1, C93.1, U9.4 (VDD), U11.10 (VDD), U12.5 (VCC), U13.8 (VCC), U19.10 (VDD), U20.5 (VCC), U22.8 (VCC); also elsewhere on the board
/PrecisionClk_N: R33.2, U9.7 (~CLK); also elsewhere on the board
/PrecisionClk_P: R33.1, U9.6 (CLK); also elsewhere on the board
/PulseOutput/Precision_CLK1_N: U9.9 (~Q3), U10.7 (~CLK)
/PulseOutput/Precision_CLK1_P: U9.10 (Q3), U10.6 (CLK)
/PulseOutput/Precision_CLK2_N: U9.11 (~Q2), U21.7 (~CLK)
/PulseOutput/Precision_CLK2_P: U9.12 (Q2), U21.6 (CLK)
/PulseOutput/Precision_CLK3_N: R34.2, U9.13 (~Q1), U11.3 (IN-)
/PulseOutput/Precision_CLK3_P: R34.1, U9.14 (Q1), U11.2 (IN+)
/PulseOutput/Precision_CLK4_N: R47.2, U9.15 (~Q0), U19.3 (IN-)
/PulseOutput/Precision_CLK4_P: R47.1, U9.16 (Q0), U19.2 (IN+)
/PulseOutput/Precision_Trigger1_N: R35.2, U10.10 (~Q), U13.3 (~D)
/PulseOutput/Precision_Trigger1_P: R36.2, U10.11 (Q), U13.2 (D)
/PulseOutput/Precision_Trigger2_N: R49.2, U21.10 (~Q), U22.3 (~D)
/PulseOutput/Precision_Trigger2_P: R50.2, U21.11 (Q), U22.2 (D)
/PulseOutput/PulseOut1: R38.1; also elsewhere on the board
/PulseOutput/PulseOut2: R51.1; also elsewhere on the board
/PulseOutput/PulseOut3: R37.1; also elsewhere on the board
/PulseOutput/PulseOut4: R48.1; also elsewhere on the board
/Trigger1_N: U10.3 (~D); also elsewhere on the board
/Trigger1_P: U10.2 (D); also elsewhere on the board
/Trigger2_N: U21.3 (~D); also elsewhere on the board
/Trigger2_P: U21.2 (D); also elsewhere on the board
/Trigger3: U12.1 (D); also elsewhere on the board
/Trigger4: U20.1 (D); also elsewhere on the board
GND: C64.2, C65.2, C66.2, C67.1, C68.2, C69.2, C89.2, C90.1, C91.2, C92.2, C93.2, D3.2 (A), D4.2 (A), D6.2 (A), D7.2 (A), U9.5 (GND), U10.9 (VEE), U10.14 (R), U10.17 (PAD), U11.1 (GND), U11.7 (GND), U12.3 (GND), U13.5 (GND), U19.1 (GND), U19.7 (GND), U20.3 (GND), U21.9 (VEE), U21.14 (R), U21.17 (PAD), U22.5 (GND); also elsewhere on the board
unnamed: D3.1 (K), R48.2, U20.4 (Q)
unnamed: D4.1 (K), R51.2, U22.7 (Q)
unnamed: D6.1 (K), R37.2, U12.4 (Q)
unnamed: D7.1 (K), R38.2, U13.7 (Q)
unnamed: U10.1 (VTD), U10.4 (~VTD)
unnamed: U10.5 (VTCLK), U10.8 (~VTCLK)
unnamed: U11.8 (OUT), U12.2 (CP)
unnamed: U19.8 (OUT), U20.2 (CP)
unnamed: U21.1 (VTD), U21.4 (~VTD)
unnamed: U21.5 (VTCLK), U21.8 (~VTCLK)

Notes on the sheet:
D-Flipflop: NB7V52MMNG Output driver: SN65LVDS4 (MC100EPT21) Fan-out buffer für den Clock: NB3L8504S Idee: Precision_clk mit NB3L8504S an zwei NB7V52MMNG verteilen (als clk) D vom FPGA Q mit MC100EPT21 in LVCMOS umwandeln
Precise trigger
Not so precise trigger
Fan-out buffer


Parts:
C1, C3, C5, C6, C8, C9, C10, C11, C12, C43, C45: 100n; C_0603_1608Metric
C2, C7: 30p; C_0603_1608Metric
C4, C42, C44: 4.7u; C_0603_1608Metric
D1, D2: PGB1010603; D_0603_1608Metric
J10: USB_C; USB_C_Receptacle_Amphenol_12401610E4-2A_CircularHoles
L4, L5: 10u; L_1008_2520Metric
R1: 10k; R_0603_1608Metric
R2: 2k; R_0603_1608Metric
R5: 12k; R_0603_1608Metric
R25, R26: 5.1k; R_0603_1608Metric
TP5, TP6, TP7, TP8, TP9, TP10, TP11, TP12, TP13, TP14, TP15, TP16, TP17: TestPoint; TestPoint_THTPad_D1.5mm_Drill0.7mm
U1: 93LC56B; SOT-23-6
U2: LM809; SOT-23
U16: FT2232HQ; QFN-64-1EP_9x9mm_P0.5mm_EP4.35x4.35mm
Y1: 12M; Crystal_SMD_5032-2Pin_5.0x3.2mm

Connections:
+3V3: C1.1, C3.1, C5.1, C8.1, C9.1, L4.1, L5.1, R1.2, U1.6 (VCC), U2.3 (VCC), U16.20 (VCCIO), U16.31 (VCCIO), U16.42 (VCCIO), U16.50 (VREGIN), U16.56 (VCCIO); also elsewhere on the board
+5VA: J10.A4 (VBUS), J10.A9 (VBUS), J10.B4 (VBUS), J10.B9 (VBUS); also elsewhere on the board
/CDR_PLL/RXD: TP10.1, U16.16 (ADBUS0); also elsewhere on the board
/CDR_PLL/TCK: TP12.1, U16.38 (BDBUS0); also elsewhere on the board
/CDR_PLL/TDI: TP9.1, U16.39 (BDBUS1); also elsewhere on the board
/CDR_PLL/TDO: TP11.1, U16.40 (BDBUS2); also elsewhere on the board
/CDR_PLL/TMS: TP13.1, U16.41 (BDBUS3); also elsewhere on the board
/Debugger/CLK: TP16.1, U1.4 (CLK), U16.62 (EECLK)
/Debugger/CS: TP17.1, U1.5 (CS), U16.63 (EECS)
/Debugger/DI: R2.1, TP15.1, U1.3 (DI), U16.61 (EEDATA)
/Debugger/DO: R1.1, R2.2, TP14.1, U1.1 (DO)
/Debugger/RXD: TP8.1, U16.17 (ADBUS1); also elsewhere on the board
/Debugger/USB_N: D2.1 (A1), J10.A7 (D-), J10.B7 (D-), U16.7 (DM)
/Debugger/USB_P: D1.1 (A1), J10.A6 (D+), J10.B6 (D+), U16.8 (DP)
/Debugger/VCORE: C4.1, C6.1, C10.1, C11.1, C12.1, TP7.1, U16.12 (VCORE), U16.37 (VCORE), U16.49 (VREGOUT), U16.64 (VCORE)
GND: C1.2, C2.2, C3.2, C4.2, C5.2, C6.2, C7.2, C8.2, C9.2, C10.2, C11.2, C12.2, C42.2, C43.2, C44.2, C45.2, D1.2 (A2), D2.2 (A2), J10.A1 (GND), J10.A12 (GND), J10.B1 (GND), J10.B12 (GND), J10.S1 (SHIELD), R5.2, R25.1, R26.1, U1.2 (GND), U2.1 (GND), U16.1 (GND), U16.5 (GND), U16.10 (AGND), U16.11 (GND), U16.13 (TEST), U16.15 (GND), U16.25 (GND), U16.35 (GND), U16.47 (GND), U16.51 (GND), U16.65 (PAD); also elsewhere on the board
unnamed: C2.1, U16.2 (OSCI), Y1.1
unnamed: C7.1, U16.3 (OSCO), Y1.2
unnamed: J10.A5 (CC1), R25.2
unnamed: J10.B5 (CC2), R26.2
unnamed: R5.1, U16.6 (REF)
unnamed: U2.2 (~RESET), U16.14 (~RESET)
VPHY: C42.1, C43.1, L5.2, TP6.1, U16.4 (VPHY)
VPLL: C44.1, C45.1, L4.2, TP5.1, U16.9 (VPLL)


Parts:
C70, C71, C72, C73, C74, C78, C79: 10u; C_0603_1608Metric
C75: 1n; C_0603_1608Metric
C76, C82, C83: 100n; C_0603_1608Metric
C77, C80, C81: 22u; C_0603_1608Metric
C84: 10p; C_0603_1608Metric
J9: Conn_01x03; PinHeader_1x03_P2.54mm_Vertical
L1, L3: 3.3u; L_Bourns-SRN8040_8x8.15mm
L2: 10u; L_1008_2520Metric
R39: 56.2k; R_0603_1608Metric
R40, R44: 10k; R_0603_1608Metric
R41: 0; R_1206_3216Metric
R42: 0; R_0603_1608Metric
R43: 30.9k; R_0603_1608Metric
TP1: +15V; TestPoint_THTPad_D1.5mm_Drill0.7mm
TP2: +3.3V; TestPoint_THTPad_D1.5mm_Drill0.7mm
TP3: +2.5V; TestPoint_THTPad_D1.5mm_Drill0.7mm
TP4: +1.8V; TestPoint_THTPad_D1.5mm_Drill0.7mm
TP18: +5V; TestPoint_THTPad_D1.5mm_Drill0.7mm
TP19, TP20, TP21: GND; TestPoint_THTPad_D1.5mm_Drill0.7mm
U14: TPS563207; SOT-563
U15: TPS62205DBV; SOT-23-5
U17: TPS563200; SOT-23-6
U18: ADM7171ACPZ-1.8-R7; LFCSP-8-1EP_3x3mm_P0.5mm_EP1.45x1.74mm

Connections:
+1V8: C79.1, TP4.1, U18.1 (VOUT), U18.2 (VOUT), U18.3 (SENSE); also elsewhere on the board
+2V5: R42.1; also elsewhere on the board
+3V3: C74.1, R41.1, U18.5 (EN), U18.7 (VIN), U18.8 (VIN); also elsewhere on the board
+5V: C71.1, C72.1, C82.1, J9.2, U14.1 (VIN), U14.5 (EN), U15.1 (VI), U15.3 (EN)
+5VA: J9.3; also elsewhere on the board
+5VD: C80.1, C81.1, J9.1, L3.2, R39.1, TP18.1
+15V: C70.1, C73.1, TP1.1, U17.3 (VIN), U17.5 (EN); also elsewhere on the board
GND: C70.2, C71.2, C72.2, C73.2, C74.2, C75.2, C77.2, C78.2, C79.2, C80.2, C81.2, C82.2, R40.2, R44.2, TP19.1, TP20.1, TP21.1, U14.3 (GND), U15.2 (GND), U17.1 (GND), U18.6 (GND), U18.9 (PAD); also elsewhere on the board
unnamed: C75.1, U18.4 (SS)
unnamed: C76.1, L3.1, U17.2 (SW)
unnamed: C76.2, U17.6 (VBST)
unnamed: C77.1, C84.1, L1.2, R41.2, R43.1, TP2.1
unnamed: C78.1, L2.2, R42.2, TP3.1, U15.4 (FB)
unnamed: C83.1, L1.1, U14.2 (SW)
unnamed: C83.2, U14.4 (BST)
unnamed: C84.2, R43.2, R44.1, U14.6 (FB)
unnamed: L2.1, U15.5 (SW)
unnamed: R39.2, R40.1, U17.4 (VFB)

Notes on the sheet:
Testpoint GND
+3.3V
Choose which 5V
+5V
+2.5V
+1.8V


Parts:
C37, C39, C40, C47, C48, C50, C51, C52, C53, C54, C56, C57: 100n; C_0402_1005Metric
C38, C41, C46, C49, C55, C58, C59, C61, C63: 100n; C_0603_1608Metric
C60, C62: 1n; C_0603_1608Metric
FB2, FB3, FB4, FB5, FB6, FB7, FB8, FB9, FB10, FB11: 30; L_0402_1005Metric
R31, R32: 0; R_0603_1608Metric
U5: MAX10M16SCE; EQFP_144
U6: SCAN921226H; BGA-49_7x7_7.0x7.0mm
U7: AD9544; LFCSP-48-1EP_7x7mm_P0.5mm_EP4.1x4.1mm

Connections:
+1V8: C37.1, C39.2, C40.1, C46.1, C47.1, C48.1, C50.2, C51.2, C52.2, C53.2, C54.1, C56.1, C57.2, FB2.1, FB3.1, FB4.1, FB5.1, FB6.1, FB7.1, U7.3 (VDDIOA), U7.6 (VDD), U7.9 (VDD), U7.28 (VDD), U7.31 (VDD), U7.34 (VDDIOB), U7.40 (VDD), U7.41 (VDD), U7.45 (VDD); also elsewhere on the board
+3V3: C38.2, C41.2, C49.2, C55.1, FB8.1, FB9.1, FB10.1, FB11.1, U5.1 (VCC_ONE), U5.2 (VCCA6), U5.5 (VCCA3), U5.34 (VCCA2), U5.35 (VCCA1), U5.36 (VCC_ONE), U5.37 (VCC_ONE), U5.51 (VCC_ONE), U5.71 (VCCA5), U5.72 (VCC_ONE), U5.73 (VCC_ONE), U5.107 (VCCA3), U5.108 (VCC_ONE), U5.109 (VCC_ONE), U5.115 (VCC_ONE), U5.143 (VCCA4), U5.144 (VCC_ONE); also elsewhere on the board
GND: C38.1, C41.1, C49.1, C55.2, C58.2, C59.1, R31.2, R32.2, U5.3 (GND), U5.4 (GND), U5.42 (GND), U5.53 (GND), U5.63 (GND), U5.68 (GND), U5.83 (GND), U5.95 (GND), U5.104 (GND), U5.116 (GND), U5.125 (GND), U5.133 (GND), U5.137 (GND), U5.142 (GND), U5.145 (PAD), U6.A1 (DGND), U6.A6 (DGND), U6.B5 (DGND), U6.D7 (DGND), U6.E4 (DGND), U6.E7 (DGND), U6.G3 (DGND); also elsewhere on the board
GNDA: C37.2, C39.1, C40.2, C46.2, C47.2, C48.2, C50.1, C51.1, C52.1, C53.1, C54.2, C56.2, C57.1, R31.1, U7.49 (EPAD); also elsewhere on the board
GNDS: C60.2, C61.1, C62.2, C63.1, R32.1, U6.A4 (AGND), U6.B2 (AGND), U6.F3 (AGND), U6.F4 (AGND), U6.G2 (AGND)
unnamed: C58.1, FB9.2, U6.C5 (DVCC), U6.C6 (DVCC), U6.D5 (DVCC)
unnamed: C59.2, FB8.2, U6.A7 (DVCC), U6.B7 (DVCC)
unnamed: C60.1, C63.2, FB11.2, U6.F1 (AVCC), U6.F2 (AVCC), U6.G1 (AVCC)
unnamed: C61.2, C62.1, FB10.2, U6.B1 (AVCC), U6.C2 (AVCC)
unnamed: FB2.2, U7.19 (VDD)
unnamed: FB3.2, U7.10 (VDD)
unnamed: FB4.2, U7.13 (VDD)
unnamed: FB5.2, U7.20 (VDD)
unnamed: FB6.2, U7.24 (VDD)
unnamed: FB7.2, U7.27 (VDD)

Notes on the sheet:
Supply SCAN921226
Supply FPGA
AD9543 Supply


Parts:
C34, C35, C36: 100n; C_0603_1608Metric
J7: Conn_01x13; PinHeader_1x13_P2.54mm_Vertical
J8: Prog.; IDC-Header_2x05_P2.54mm_Vertical
J11, J12, J13: Conn_01x02; TerminalBlock_Phoenix_MKDS-1,5-2-5.08_1x02_P5.08mm_Horizont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
Q1, Q2, Q3: BSS123; SOT-23
R18, R20, R24, R27, R28, R29: 10k; R_0603_1608Metric
R19, R23: 1k; R_0603_1608Metric
R21, R22, R30: R; R_0603_1608Metric
U5: MAX10M16SCE; EQFP_144

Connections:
+3V3: C34.1, C35.2, C36.2, J7.1, J8.4, R18.1, R20.1, R21.1, R22.1, R24.1, R27.1, R28.1, R30.1, U5.9 (VCCIO1A), U5.23 (VCCIO1B), U5.31 (VCCIO2), U5.82 (VCCIO5), U5.122 (DEV_OE), U5.128 (VCCIO8), U5.139 (VCCIO8); also elsewhere on the board
/CDR_PLL/Programming_Unused/IO0: J7.2, U5.74 (IO)
/CDR_PLL/Programming_Unused/IO1: J7.3, U5.75 (IO/RUP)
/CDR_PLL/Programming_Unused/IO2: J7.4, U5.76 (IO)
/CDR_PLL/Programming_Unused/IO3: J7.5, U5.77 (IO/RDN)
/CDR_PLL/Programming_Unused/IO4: J7.6, U5.78 (IO)
/CDR_PLL/Programming_Unused/IO5: J7.7, U5.79 (IO)
/CDR_PLL/Programming_Unused/IO6: J7.8, U5.81 (IO)
/CDR_PLL/Programming_Unused/IO7: J7.9, U5.84 (IO)
/CDR_PLL/Programming_Unused/IO8: J7.10, U5.85 (IO)
/CDR_PLL/Programming_Unused/IO9: J7.11, U5.86 (IO)
/CDR_PLL/Programming_Unused/IO10: J7.12, U5.87 (IO)
/CDR_PLL/Programming_Unused/LED_1: Q1.1 (G), U5.33 (IO/PLL_L_CLKOUTp)
/CDR_PLL/Programming_Unused/LED_2: Q2.1 (G), U5.26 (IO/CLK0n)
/CDR_PLL/Programming_Unused/LED_3: Q3.1 (G), U5.27 (IO/CLK0p)
/CDR_PLL/RXD: U5.141 (IO); also elsewhere on the board
/CDR_PLL/TCK: U5.132 (IO); also elsewhere on the board
/CDR_PLL/TDI: U5.130 (IO); also elsewhere on the board
/CDR_PLL/TDO: U5.131 (IO); also elsewhere on the board
/CDR_PLL/TMS: U5.127 (IO); also elsewhere on the board
/Debugger/RXD: U5.140 (IO); also elsewhere on the board
Clk_40MHz: U5.120 (IO); also elsewhere on the board
GND: C34.2, C35.1, C36.1, J7.13, J8.2, J8.10, Q1.2 (S), Q2.2 (S), Q3.2 (S), R19.2, R23.1, R29.1, U5.121 (DEV_CLRn); also elsewhere on the board
unnamed: J8.1, R19.1, U5.18 (TCK)
unnamed: J8.3, U5.20 (TDO)
unnamed: J8.5, R20.2, U5.16 (TMS)
unnamed: J8.9, R18.2, U5.19 (TDI)
unnamed: J11.1, R21.2
unnamed: J11.2, Q1.3 (D)
unnamed: J12.1, R22.2
unnamed: J12.2, Q2.3 (D)
unnamed: J13.1, R30.2
unnamed: J13.2, Q3.3 (D)
unnamed: R23.2, U5.15 (JTAGEN)
unnamed: R24.2, U5.136 (nSTATUS)
unnamed: R27.2, U5.138 (CONF_DONE)
unnamed: R28.2, U5.129 (nCONFIG)
unnamed: R29.2, U5.126 (CONFIG_SEL)

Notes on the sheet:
Programming - FPGA
Unused
Debugging purpose
Programming - FT2232 40MHz Clock


Board: 4 copper layers, 160.0 x 100.0 mm, 239 parts (0 on the bottom side), 176 nets.

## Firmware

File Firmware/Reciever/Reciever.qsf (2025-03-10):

# -------------------------------------------------------------------------- #
#
# Copyright (C) 2020  Intel Corporation. All rights reserved.
# Your use of Intel Corporation's design tools, logic functions 
# and other software and tools, and any partner logic 
# functions, and any output files from any of the foregoing 
# (including device programming or simulation files), and any 
# associated documentation or information are expressly subject 
# to the terms and conditions of the Intel Program License 
# Subscription Agreement, the Intel Quartus Prime License Agreement,
# the Intel FPGA IP License Agreement, or other applicable license
# agreement, including, without limitation, that your use is for
# the sole purpose of programming logic devices manufactured by
# Intel and sold by Intel or its authorized distributors.  Please
# refer to the applicable agreement for further details, at
# https://fpgasoftware.intel.com/eula.
#
# -------------------------------------------------------------------------- #
#
# Quartus Prime
# Version 20.1.0 Build 711 06/05/2020 SJ Lite Edition
# Date created = 17:26:31  Juli 08, 2021
#
# -------------------------------------------------------------------------- #
#
# Notes:
#
# 1) The default values for assignments are stored in the file:
#		Reciever_assignment_defaults.qdf
#    If this file doesn't exist, see file:
#		assignment_defaults.qdf
#
# 2) Altera recommends that you do not modify this file. This
#    file is updated automatically by the Quartus Prime software
#    and any changes you make may be lost or overwritten.
#
# -------------------------------------------------------------------------- #


set_global_assignment -name FAMILY "MAX 10"
set_global_assignment -name DEVICE 10M16SCE144A7G
set_global_assignment -name TOP_LEVEL_ENTITY Reciever
set_global_assignment -name ORIGINAL_QUARTUS_VERSION 20.1.0
set_global_assignment -name PROJECT_CREATION_TIME_DATE "17:26:31  JULI 08, 2021"
set_global_assignment -name LAST_QUARTUS_VERSION "23.1std.0 Lite Edition"
set_global_assignment -name PROJECT_OUTPUT_DIRECTORY output_files
set_global_assignment -name MIN_CORE_JUNCTION_TEMP "-40"
set_global_assignment -name MAX_CORE_JUNCTION_TEMP 125
set_global_assignment -name DEVICE_FILTER_PACKAGE EQFP
set_global_assignment -name DEVICE_FILTER_PIN_COUNT 144
set_global_assignment -name ERROR_CHECK_FREQUENCY_DIVISOR 256
set_global_assignment -name PARTITION_NETLIST_TYPE SOURCE -section_id Top
set_global_assignment -name PARTITION_FITTER_PRESERVATION_LEVEL PLACEMENT_AND_ROUTING -section_id Top
set_global_assignment -name PARTITION_COLOR 16764057 -section_id Top
set_location_assignment PIN_119 -to RESETn
set_instance_assignment -name IO_STANDARD "1.8 V" -to RESETn
set_location_assignment PIN_120 -to clk_40Mhz
set_location_assignment PIN_87 -to GPIO[10]
set_location_assignment PIN_86 -to GPIO[9]
set_location_assignment PIN_85 -to GPIO[8]
set_location_assignment PIN_84 -to GPIO[7]
set_location_assignment PIN_81 -to GPIO[6]
set_location_assignment PIN_79 -to GPIO[5]
set_location_assignment PIN_78 -to GPIO[4]
set_location_assignment PIN_77 -to GPIO[3]
set_location_assignment PIN_76 -to GPIO[2]
set_location_assignment PIN_75 -to GPIO[1]
set_location_assignment PIN_74 -to GPIO[0]
set_location_assignment PIN_106 -to LOCKn
set_location_assignment PIN_90 -to RCLKRf
set_location_assignment PIN_92 -to deserialized[0]
set_location_assignment PIN_93 -to deserialized[1]
set_location_assignment PIN_91 -to deserialized[2]
set_location_assignment PIN_96 -to deserialized[3]
set_location_assignment PIN_98 -to deserialized[4]
set_location_assignment PIN_99 -to deserialized[5]
set_location_assignment PIN_100 -to deserialized[6]
set_location_assignment PIN_102 -to deserialized[7]
set_location_assignment PIN_101 -to deserialized[8]
set_location_assignment PIN_105 -to deserialized[9]
set_location_assignment PIN_89 -to word_clk
set_location_assignment PIN_56 -to clk_40Mhz_2

set_global_assignment -name POWER_PRESET_COOLING_SOLUTION "23 MM HEAT SINK WITH 200 LFPM AIRFLOW"
set_global_assignment -name POWER_BOARD_THERMAL_MODEL "NONE (CONSERVATIVE)"
set_global_assignment -name FLOW_ENABLE_POWER_ANALYZER ON
set_global_assignment -name POWER_DEFAULT_INPUT_IO_TOGGLE_RATE "12.5 %"
set_location_assignment PIN_88 -to slow_data
set_location_assignment PIN_65 -to trigger1
set_location_assignment PIN_59 -to trigger3
set_location_assignment PIN_141 -to RX
set_location_assignment PIN_140 -to TX
set_location_assignment PIN_110 -to SPI_Timer_CSB
set_location_assignment PIN_113 -to SPI_Timer_SCLK
set_location_assignment PIN_111 -to SPI_Timer_SDI
set_location_assignment PIN_114 -to SPI_Timer_SDO
set_instance_assignment -name IO_STANDARD "1.8 V" -to SPI_Timer_CSB
set_instance_assignment -name IO_STANDARD "1.8 V" -to SPI_Timer_SCLK
set_instance_assignment -name IO_STANDARD "1.8 V" -to SPI_Timer_SDI
set_instance_assignment -name IO_STANDARD "1.8 V" -to SPI_Timer_SDO
set_location_assignment PIN_60 -to trigger4
set_instance_assignment -name IO_STANDARD LVDS -to trigger1
set_location_assignment PIN_64 -to "trigger1(n)"
set_location_assignment PIN_70 -to trigger2
set_instance_assignment -name IO_STANDARD LVDS -to trigger2
set_location_assignment PIN_69 -to "trigger2(n)"
set_location_assignment PIN_118 -to pll_locked
set_location_assignment PIN_33 -to led1
set_location_assignment PIN_26 -to led2
set_location_assignment PIN_27 -to led3
set_instance_assignment -name IO_STANDARD "1.8 V" -to pll_locked
set_location_assignment PIN_43 -to serial_o1
set_location_assignment PIN_50 -to serial_o2
set_location_assignment PIN_41 -to serial_o3
set_location_assignment PIN_47 -to serial_o4
set_global_assignment -name SYSTEMVERILOG_FILE ../general/watchdog/Watchdog.sv
set_global_assignment -name SYSTEMVERILOG_FILE ../general/SlowLink/Transmitter2/SlowTransmitter2.sv
set_global_assignment -name SYSTEMVERILOG_FILE ../general/PayloadTransmitter/PayloadTransmitter.sv
set_global_assignment -name SYSTEMVERILOG_FILE ../general/Trigger/LongDivision.sv
set_global_assignment -name SYSTEMVERILOG_FILE ../general/Trigger/Delay.sv
set_global_assignment -name SYSTEMVERILOG_FILE pulse_extender.sv
set_global_assignment -name SYSTEMVERILOG_FILE ../general/Trigger/Trigger.sv
set_global_assignment -name SYSTEMVERILOG_FILE crc_calc.sv
set_global_assignment -name SYSTEMVERILOG_FILE FrameReceiver.sv
set_global_assignment -name SYSTEMVERILOG_FILE ../general/protocol/data_frames.sv
set_global_assignment -name SYSTEMVERILOG_FILE fifo_v3.sv
set_global_assignment -name VERILOG_FILE Encode_8b10b.v
set_global_assignment -name SYSTEMVERILOG_FILE APB/ApbBus.sv
set_global_assignment -name QIP_FILE ROM/synthesis/ROM.qip
set_global_assignment -name VERILOG_FILE ROM/synthesis/ROM.v -library ROM
set_global_assignment -name VERILOG_FILE Softcore/VexRISCVSoftcore.v
set_global_assignment -name SDC_FILE Timing.sdc
set_global_assignment -name VERILOG_FILE Decode_8b10b.v
set_global_assignment -name SYSTEMVERILOG_FILE Reciever.sv
set_instance_assignment -name PARTITION_HIERARCHY root_partition -to | -section_id Top

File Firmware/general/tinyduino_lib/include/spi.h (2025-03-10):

/*

MIT License

Copyright (c) 2021 Domenic Wüthrich, Manuel Eggimann, Yves Acremann (ETH Zurich)

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
*/

#ifndef SPI_H_
#define SPI_H_

#include "type.h"
#include "io.h"

#define SPI_DATA        0x00
#define SPI_BUFFER      0x04
#define SPI_CONFIG      0x08
#define SPI_INTERRUPT   0x0C
#define SPI_CLK_DIVIDER 0x20
#define SPI_SS_SETUP    0x24
#define SPI_SS_HOLD     0x28
#define SPI_SS_DISABLE  0x2C

typedef struct {
    u32 cpol;
    u32 cpha;
    u32 mode;
    u32 clkDivider;
    u32 ssSetup;
    u32 ssHold;
    u32 ssDisable;
} Spi_Config;

#define SPI_CMD_WRITE (1 << 8)
#define SPI_CMD_READ (1 << 9)
#define SPI_CMD_SS (1 << 11)

#define SPI_RSP_VALID (1 << 31)

#define SPI_STATUS_CMD_INT_ENABLE = (1 << 0)
#define SPI_STATUS_RSP_INT_ENABLE = (1 << 1)
#define SPI_STATUS_CMD_INT_FLAG = (1 << 8)
#define SPI_STATUS_RSP_INT_FLAG = (1 << 9)


#define SPI_MODE_CPOL (1 << 0)
#define SPI_MODE_CPHA (1 << 1)


u32 spi_cmdAvailability(u32 reg);

u32 spi_rspOccupancy(u32 reg);

void spi_write(u32 reg, u8 data);

u8 spi_writeRead(u32 reg, u8 data);


u8 spi_read(u32 reg);

void spi_select(u32 reg, u32 slaveId);

void spi_diselect(u32 reg, u32 slaveId);

void spi_applyConfig(u32 reg, Spi_Config *config);

#endif /* SPI_H_ */

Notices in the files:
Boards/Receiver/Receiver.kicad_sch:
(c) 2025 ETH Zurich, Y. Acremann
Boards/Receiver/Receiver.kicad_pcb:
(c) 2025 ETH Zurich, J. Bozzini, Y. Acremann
